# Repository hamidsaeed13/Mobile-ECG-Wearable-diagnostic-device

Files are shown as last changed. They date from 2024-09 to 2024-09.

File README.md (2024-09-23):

# Mobile ECG Project

### Supervisor:
-Prof. Dr. Shahid Khattak

### Team Members:
- Abdul Hameed
- M. Hamid Saeed
- Mujahid Haider

---

## Introduction:
This project aims to create a healthcare wearable Clinical Grade ECG device for continuous heart monitoring.
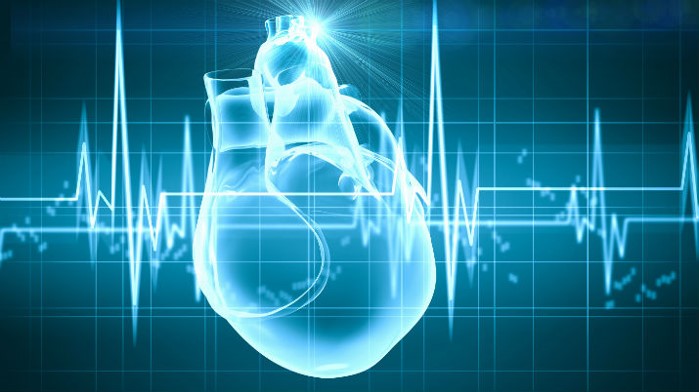
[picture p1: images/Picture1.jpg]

## Motivation:
- Existing ECG solutions are large and costly.
- Patients must be hospitalized, making it difficult to maintain long-term ECG logs.
- 24/7 ECG monitoring in remote areas is a challenge.

## Our Solution:
- 10-lead, 12-channel ECG diagnostic device.
- Bluetooth-enabled data transmission to smartphones for processing and log maintenance.
 
| Mobile Application | Demo Product |

---

## Aims and Objectives:
- Signal acquisition and conditioning.
- Multiplexing and Bluetooth communication.
- Real-time ECG graph visualization.
- Log maintenance and record-sharing with cardiologists.

---

## System Block Diagram:
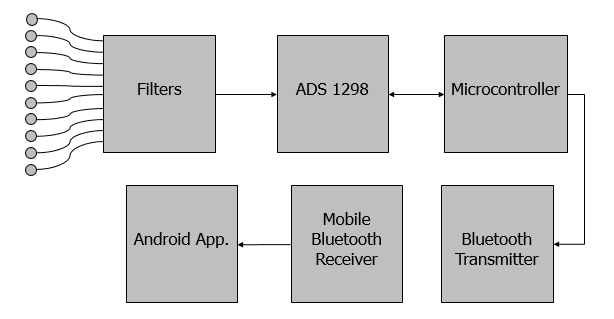
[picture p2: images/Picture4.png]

---
## Our Project:
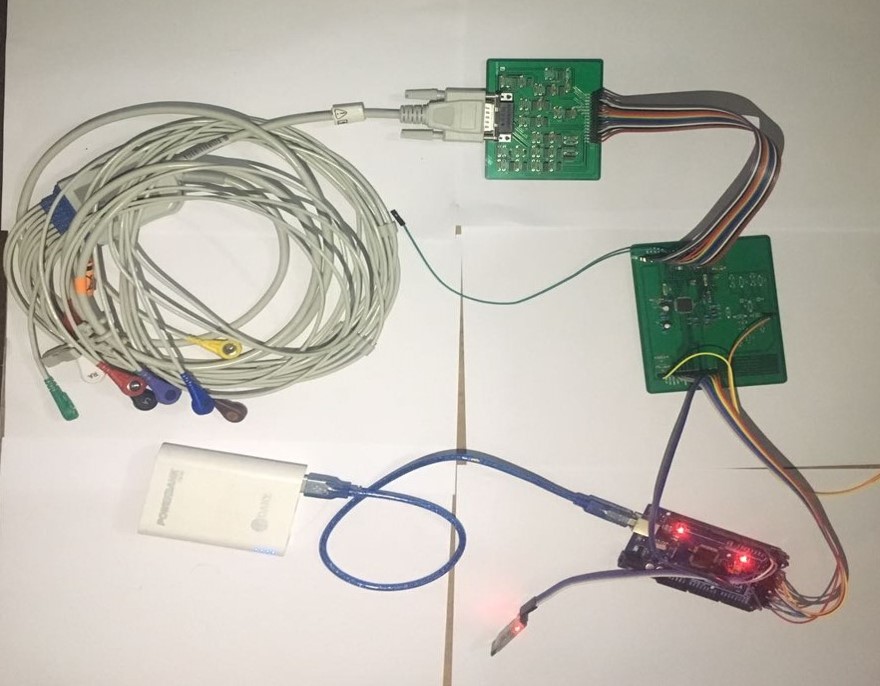
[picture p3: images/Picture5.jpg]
Project


---
## Filter Design:
- **Schematic**: 
  - R1 = 142.1KΩ
  - R2 = 120KΩ
  - C1 = C2 = 10nF
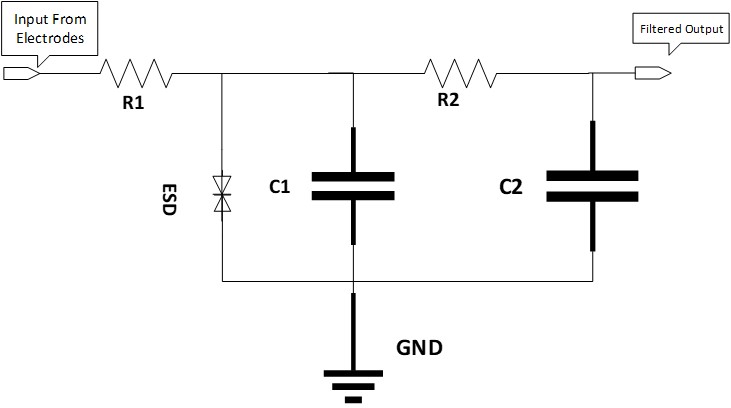
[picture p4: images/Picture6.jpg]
- **Design**: 
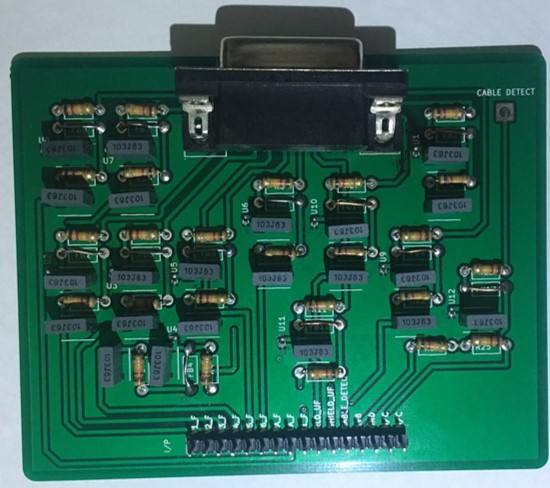
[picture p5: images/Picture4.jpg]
- **PCB**: 

---

## ADS1298:
- **Breakout Board**: 
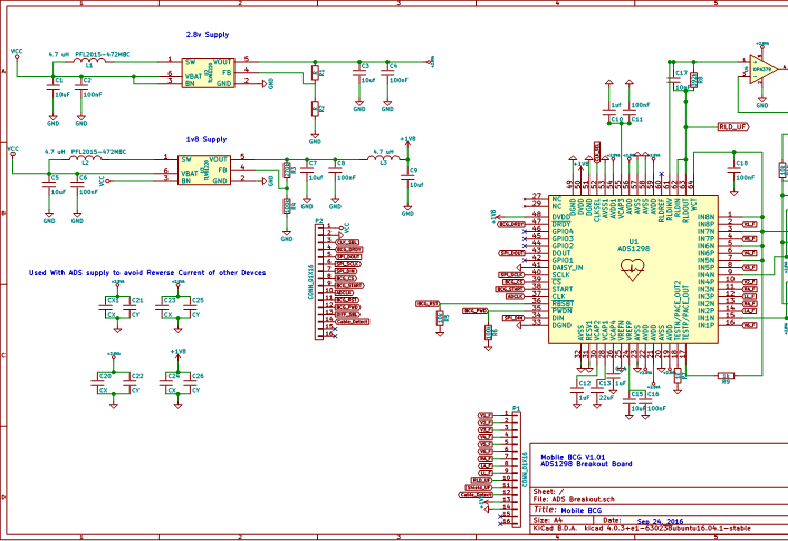
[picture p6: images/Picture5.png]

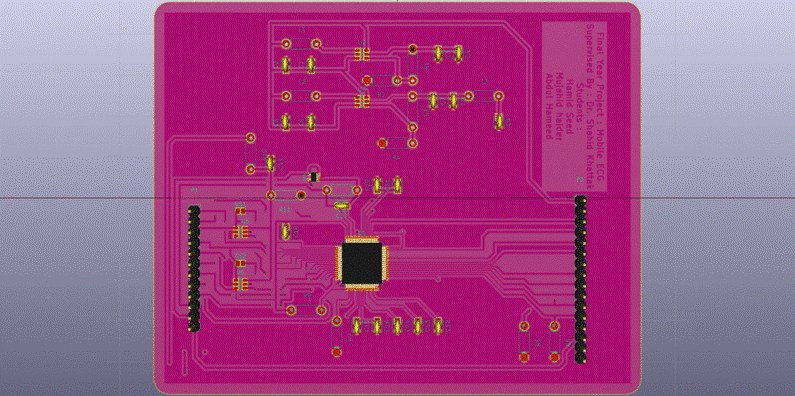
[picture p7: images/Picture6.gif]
- **PCB Layout**: 

---

## Android Application:
- Features:
  - Navigation menu with user details, doctor communication, and log maintenance.
  - 12-channel ECG view, Bluetooth connection, and real-time communication.
  - Options to find doctors and maintain a patient history.

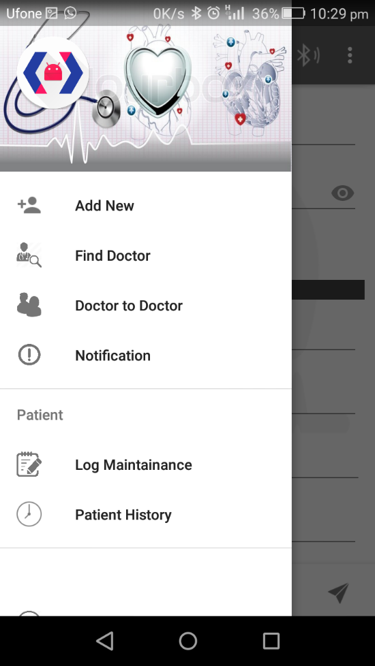
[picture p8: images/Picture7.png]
    
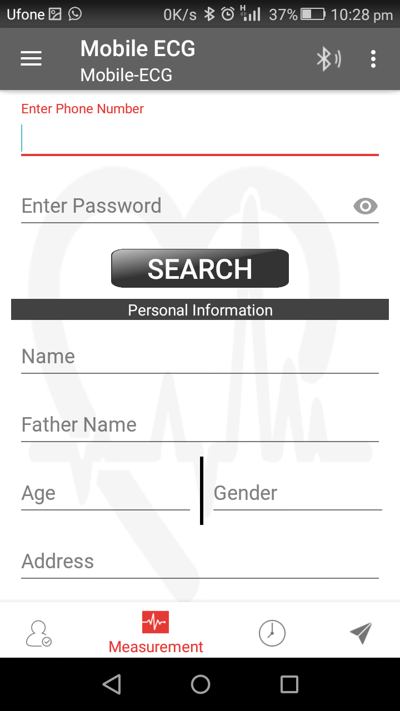
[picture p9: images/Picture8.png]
   
  
  
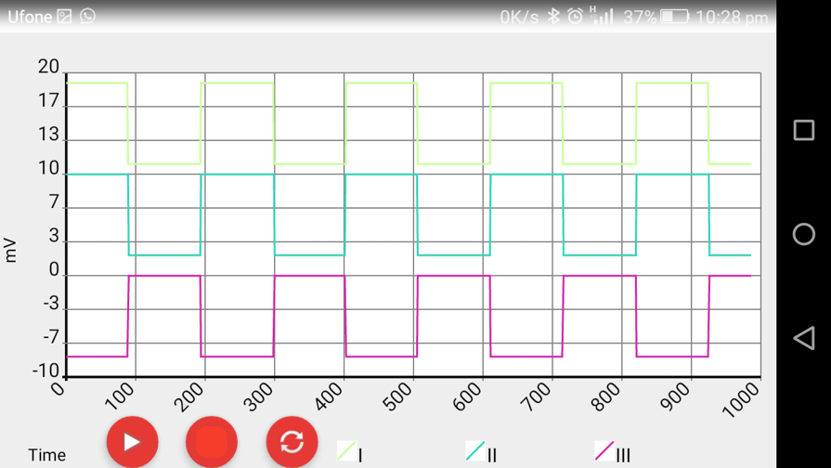
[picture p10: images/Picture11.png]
  
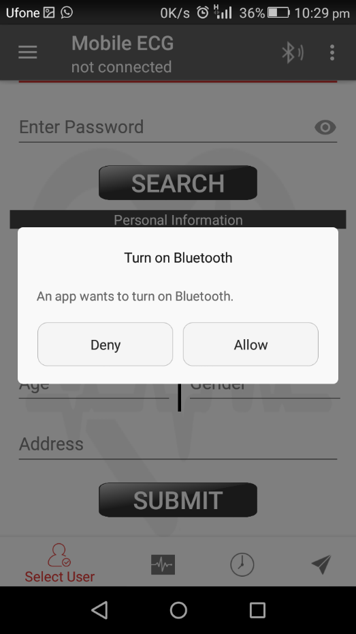
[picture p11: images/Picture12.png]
  
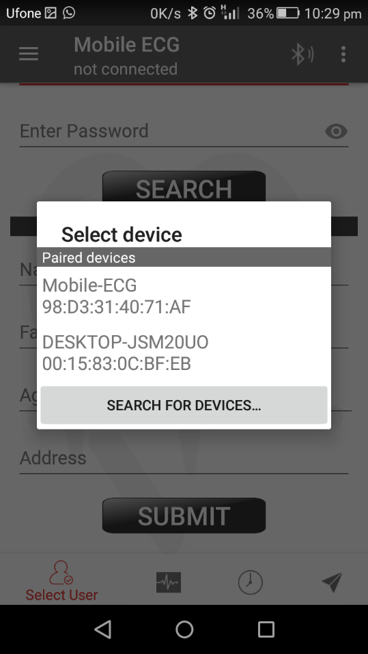
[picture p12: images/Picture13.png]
  
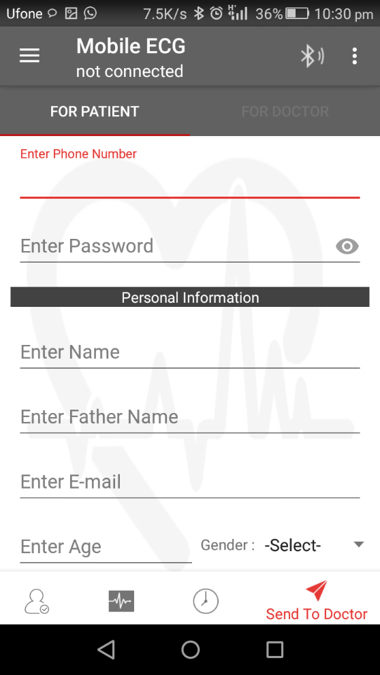
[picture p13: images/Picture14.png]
  
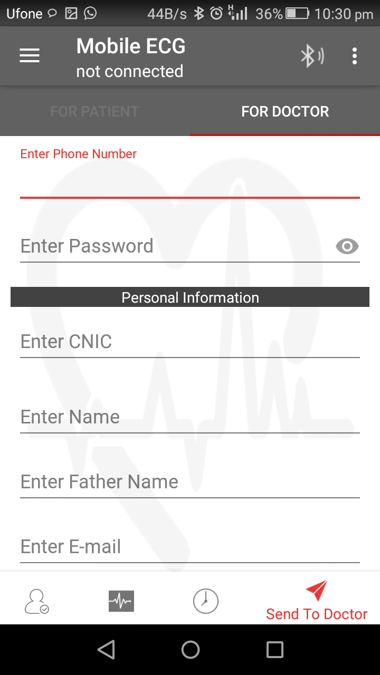
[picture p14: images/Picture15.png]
  
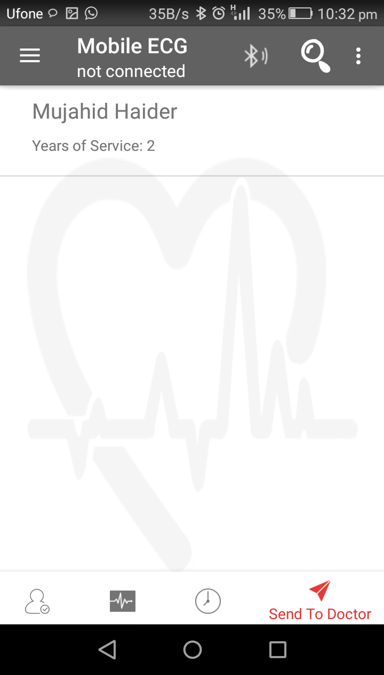
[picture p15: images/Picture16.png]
   

---
## Database
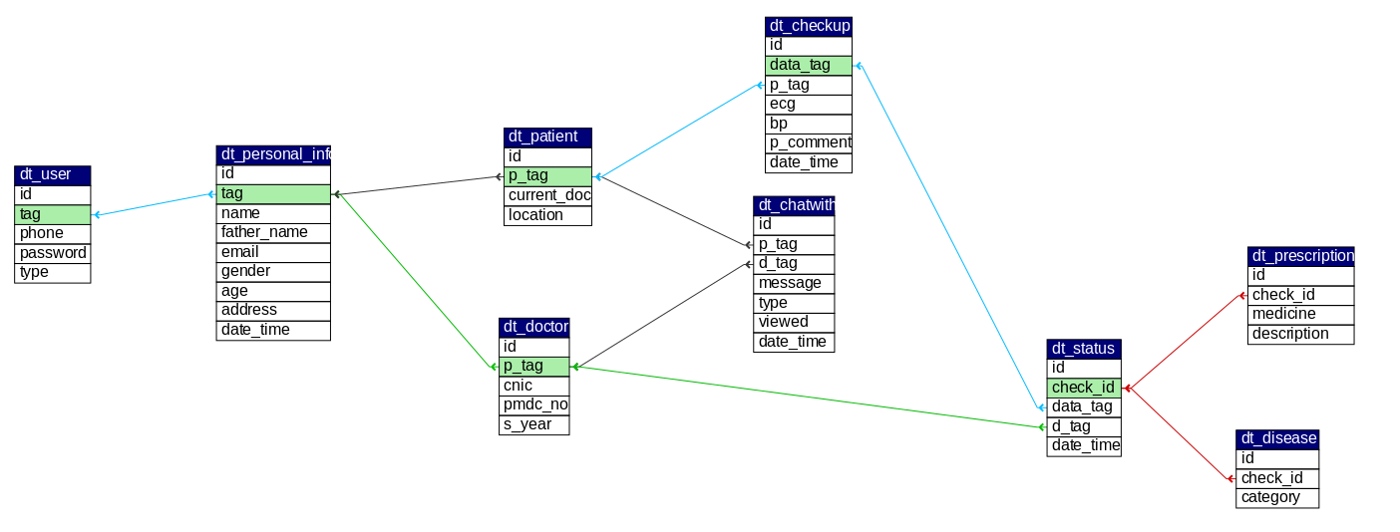
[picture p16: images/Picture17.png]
   

---

## Working Schedule:
- Phase I (March 2016 - May 2016)
- Phase II (August 2016 - Onwards)

---

## Questions:
Feel free to reach out for further details.
*contact*: +92301 2216201
email: hamidsaeed13@gmail.com

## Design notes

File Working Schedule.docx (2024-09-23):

# FYP Title: Mobile ECG

# Objectives:

Make wearable Hardware Device to Acquire ECG Signal, Transfer this signal to Android Mobile. Real time ECG Monitoring. Apply Signal Conditioning Algorithms. Maintaining Log of ECG Signal and send to a heart Specialist

We are going to provide basic 3 facilities

1. Home ECG Service

This service will allow patients to provide their doctors with frequent, reliable high-quality records. Also check out our affordable clinical-grade device designed for doctors and patients.

2. Interpretation Service

Have your ECG record (and medical history) analyzed over the internet by the heart specialist of your choice.

3. Doctor-to-doctor Service

This service will allow other doctors to send data to heart specialists and have a consultation with them.

# Schedule of Phase 1

Start | End | | Presentation on ADS1298
03-03-16 | 06-04-16 | Bluetooth interfacing | | Graph View
06-04-16 | 19-04-16 | Layout of Application
19-04-16 | 26-04-16 | | | send data from Arduino to android
26-04-16 | 03-05-16 | Circular buffer | | MATLAB implementation of signal reconditioning
26-04-16 | 10-05-16 | Filter Simulation of 3-lead
10-05-16 | 17-05-16 | Filter simulation and Power Supply for ADS
17-05-16 | 31-05-16 | Instrumentation amplifier design
01-06-16 | 10-06-16 | programming of microcontroller for ADS | View ECG signal on android app
01-06-16 | 25-06-16 | setting of ADS ,signal input ,Power supply

End of Semester

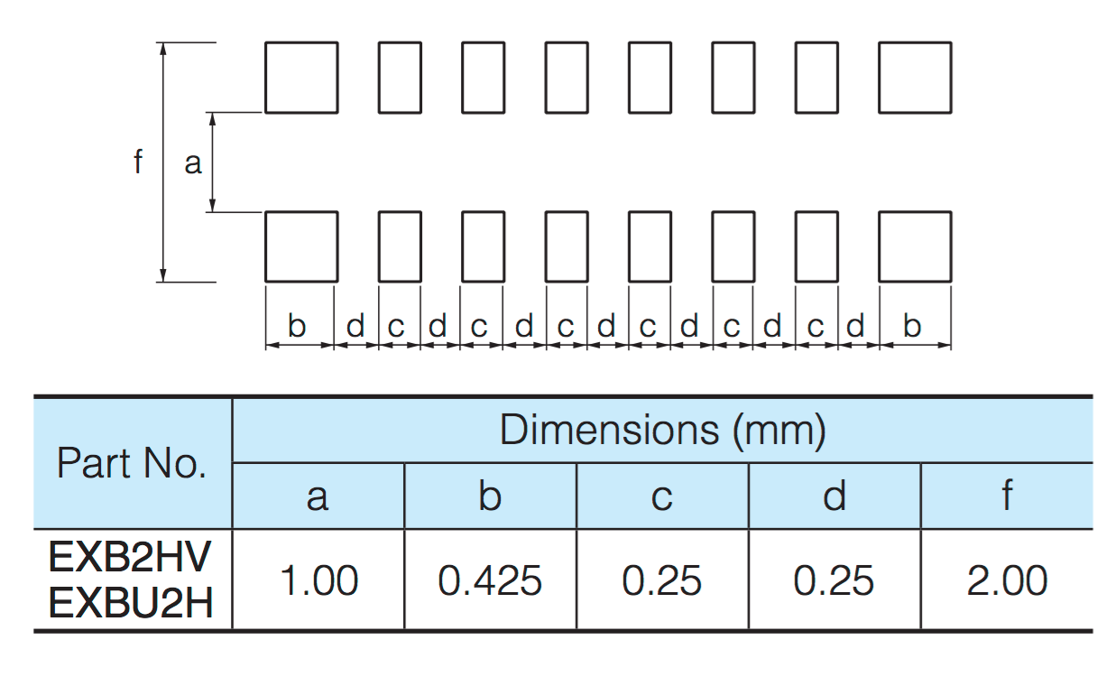
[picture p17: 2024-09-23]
Mobile ECG Hardware Final/Hardware/Datasheets/Resistor network/EXB2HV.png

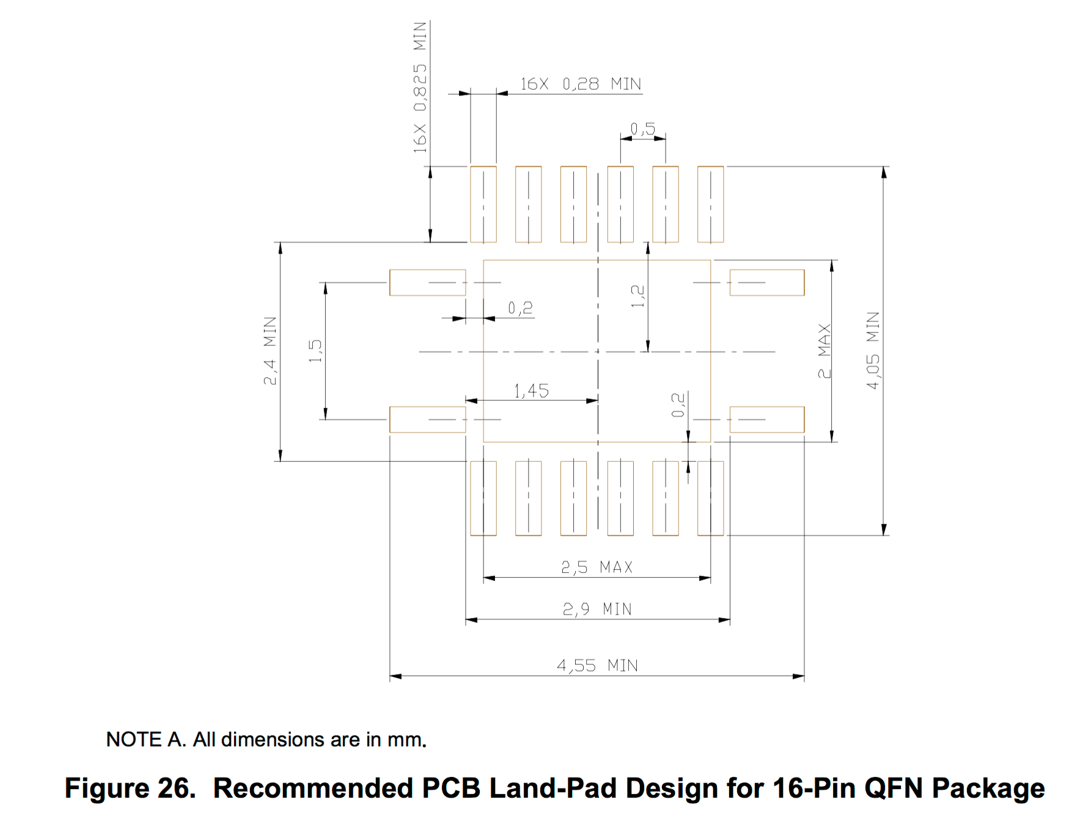
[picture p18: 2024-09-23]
Mobile ECG Hardware Final/Hardware/Datasheets/Level shifter/Footprint.png

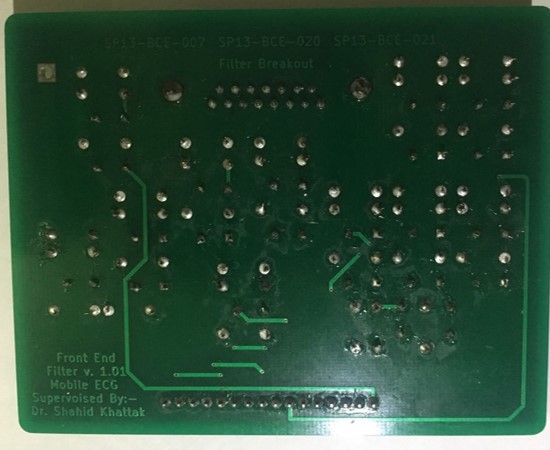
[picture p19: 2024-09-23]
images/Picture7.jpg

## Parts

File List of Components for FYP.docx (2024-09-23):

Name | Qty | $ | Search Link
INA333 | 3 | 4.42 | Digi key Part No : 296-23564-1-ND (http://www.digikey.com/product-detail/en/texas-instruments/INA333AIDGKR/296-23564-1-ND/1886116) Manufacturer No: INA333AIDGKR (http://www.digikey.com/product-detail/en/texas-instruments/INA333AIDGKR/296-23564-1-ND/1886116)
HDMI 12 lead ECG/EKG Cable with lead wires | 1 | 35
ECG/EKG electrodes adapter | 12 | -
ADS1298 | 2 | 41.81 | Digi key Part No : 296-27734-ND (http://www.digikey.com/product-detail/en/texas-instruments/ADS1298IPAG/296-27734-ND/2360825) Manufacturer No: ADS1298IPAG (http://www.digikey.com/product-detail/en/texas-instruments/ADS1298IPAG/296-27734-ND/2360825)
KIT PERFORMANCE DEMO FOR ADS1298 | 1 | 200.56 | Digi key Part No : 296-30132-ND (http://www.digikey.com/product-detail/en/texas-instruments/ADS1298ECGFE-PDK/296-30132-ND/2353228) Manufacturer No: ADS1298ECGFE-PDK (http://www.digikey.com/product-detail/en/texas-instruments/ADS1298ECGFE-PDK/296-30132-ND/2353228)
TQFP64 adapter IC test socket | 1 | 18.68 | Search Link (http://www.ebay.com/itm/QFP64-TQFP64-adapter-IC-test-socket-burning-seat-0-5m-programmer-LQFP64-seat-/351518438484)
HDMI Connector | 3 | 0.73 | Digi key Part No : 609-4614-1-ND (http://www.digikey.com/product-detail/en/amphenol-fci/10029449-111RLF/609-4614-1-ND/2785376) Manufacturer No: 10029449-111RLF (http://www.digikey.com/product-detail/en/amphenol-fci/10029449-111RLF/609-4614-1-ND/2785376)
TiWi-uB2 (Bluetooth Module) | 1 | 12.30 | Digi key Part No : 450-0104-ND (http://www.digikey.com/product-detail/en/lsr/450-0104/450-0104-ND/3661880) Manufacturer No: 450-0104 (http://www.digikey.com/product-detail/en/lsr/450-0104/450-0104-ND/3661880)
TXB0106PWR (Bidirectional Voltage-Level Translator) | 3 | 1.92 | Digi key Part No : 296-23759-1-ND (http://www.digikey.com/product-detail/en/texas-instruments/TXB0106PWR/296-23759-1-ND/1951146) Manufacturer No: TXB0106PWR (http://www.digikey.com/product-detail/en/texas-instruments/TXB0106PWR/296-23759-1-ND/1951146)
STM32F4 01/11 Microcontroller | 2 | 6.25 | Digi key Part No : 497-14047-ND (http://www.digikey.com/product-detail/en/stmicroelectronics/STM32F401RCT6/497-14047-ND/4494300) / 497-14909-ND (http://www.digikey.com/product-detail/en/stmicroelectronics/STM32F411RET6/497-14909-ND/4935722) Manufacturer No: STM32F401RCT6 (http://www.digikey.com/product-detail/en/stmicroelectronics/STM32F401RCT6/497-14047-ND/4494300)/ STM32F411RET6 (http://www.digikey.com/product-detail/en/stmicroelectronics/STM32F411RET6/497-14909-ND/4935722)
BOARD NUCLEO STM32F4 01/11 SERIES | 1 | 13.83 | Digi key Part No : 497-14360-ND (http://www.digikey.com/product-detail/en/stmicroelectronics/NUCLEO-F401RE/497-14360-ND/4695525) / 497-14711-ND (http://www.digikey.com/product-detail/en/stmicroelectronics/NUCLEO-F411RE/497-14711-ND/4866485) Manufacturer No: NUCLEO-F401RE (http://www.digikey.com/product-detail/en/stmicroelectronics/NUCLEO-F401RE/497-14360-ND/4695525) / NUCLEO-F411RE (http://www.digikey.com/product-detail/en/stmicroelectronics/NUCLEO-F411RE/497-14711-ND/4866485)
USB2641 Flash Memory for Controller | 1 | 3.18 | Digi key Part No : USB2641-HZH-02-ND (http://www.digikey.com/product-detail/en/microchip-technology/USB2641-HZH-02/USB2641-HZH-02-ND/3873174) Manufacturer No: USB2641-HZH-02 (http://www.digikey.com/product-detail/en/microchip-technology/USB2641-HZH-02/USB2641-HZH-02-ND/3873174)
LIS2DH12TR | 1 | 1.60 | Digi key Part No : 497-14851-1-ND (http://www.digikey.com/product-detail/en/stmicroelectronics/LIS2DH12TR/497-14851-1-ND/4899838) Manufacturer No: LIS2DH12TR (http://www.digikey.com/product-detail/en/stmicroelectronics/LIS2DH12TR/497-14851-1-ND/4899838)
ESD suppressor | 20 | 0.47 | Digi key Part No : 296-30406-1-ND (http://www.digikey.com/product-detail/en/texas-instruments/TPD1E10B06DPYR/296-30406-1-ND/3283560) Manufacturer No: TPD1E10B06DPYR (http://www.digikey.com/product-detail/en/texas-instruments/TPD1E10B06DPYR/296-30406-1-ND/3283560)
TS5A3159 | 3 | 0.85 | Digi key Part No : 296-19265-1-ND (http://www.digikey.com/product-detail/en/texas-instruments/TS5A3159ADBVR/296-19265-1-ND/936397) Manufacturer No: TS5A3159ADBVR (http://www.digikey.com/product-detail/en/texas-instruments/TS5A3159ADBVR/296-19265-1-ND/936397)
OPA2379 | 2 | 1.41 | Digi key Part No : 296-19875-1-ND (http://www.digikey.com/product-detail/en/texas-instruments/OPA379AIDCKT/296-19875-1-ND/1120791) Manufacturer No: OPA379AIDCKT (http://www.digikey.com/product-detail/en/texas-instruments/OPA379AIDCKT/296-19875-1-ND/1120791)
USBULC6-2M6 | 2 | 1.21 | Digi key Part No : 497-7044-1-ND (http://www.digikey.com/product-detail/en/stmicroelectronics/USBULC6-2M6/497-7044-1-ND/1880382) Manufacturer No: USBULC6-2M6 (http://www.digikey.com/product-detail/en/stmicroelectronics/USBULC6-2M6/497-7044-1-ND/1880382)
AB38T-32.768KHZ (XT oscillator) | 2 | 0.57 | Digi key Part No : 300-8340-1-ND (http://www.digikey.com/product-detail/en/citizen-finedevice-co-ltd/CMR200T32768DZFT/300-8340-1-ND/862984) Manufacturer No: CMR200T32768DZFT (http://www.digikey.com/product-detail/en/citizen-finedevice-co-ltd/CMR200T32768DZFT/300-8340-1-ND/862984)
CRYSTAL 10MHz | 2 | 0.28 | Digi key Part No : 535-9065-1-ND (http://www.digikey.com/product-detail/en/abracon-llc/ABLS-10.000MHZ-B2-T/535-9065-1-ND/675582) Manufacturer No: ABLS-10.000MHZ-B2-T (http://www.digikey.com/product-detail/en/abracon-llc/ABLS-10.000MHZ-B2-T/535-9065-1-ND/675582)
EXB-2HV510JV (Resistor Array 51ohm) | 5 | 0.037 | Digi key Part No : EXB-2HV510JV-ND (http://www.digikey.com/product-search/en?keywords=%20EXB-2HV510JV) Manufacturer No: EXB-2HV510JV (http://www.digikey.com/product-search/en?keywords=%20EXB-2HV510JV)
2450AT42A100E (Bluetooth Antenna) | 2 | 1.10 | Digi key Part No : 712-1007-1-ND (http://www.digikey.com/product-detail/en/johanson-technology-inc/2450AT42A100E/712-1007-1-ND/1560836) Manufacturer No: 2450AT42A100E (http://www.digikey.com/product-detail/en/johanson-technology-inc/2450AT42A100E/712-1007-1-ND/1560836)
EXB2HV104JV (Resistor Array 100 ohm) | 2 | 0.55 | Digi key Part No : Y1104CT-ND (http://www.digikey.com/product-detail/en/panasonic-electronic-components/EXB-2HV104JV/Y1104CT-ND/285405) Manufacturer No: EXB-2HV104JV (http://www.digikey.com/product-detail/en/panasonic-electronic-components/EXB-2HV104JV/Y1104CT-ND/285405)
uSD MicroSD Connector | 1 | 1.11 | Part No : MEM2051-00-195-00-A (http://www.newark.com/jsp/search/productdetail.jsp?sku=05W3557) (http://www.digikey.com/product-detail/en/panasonic-electronic-components/EXB-2HV104JV/Y1104CT-ND/285405)
AT24CS01-STUM-T (EEPROM 1KBIT) | 1 | 0.33 | Digi key Part No : AT24CS01-STUM-TCT-ND (http://www.digikey.com/product-detail/en/atmel/AT24CS01-STUM-T/AT24CS01-STUM-TCT-ND/3973039) Manufacturer No: AT24CS01-STUM-T (http://www.digikey.com/product-detail/en/atmel/AT24CS01-STUM-T/AT24CS01-STUM-TCT-ND/3973039)
CRYSTAL 24MHz | 2 | 0.44 | Digi key Part No : 535-9881-1-ND (http://www.digikey.com/product-detail/en/abracon-llc/ABLS2-24.000MHZ-D4YF-T/535-9881-1-ND/2001504) Manufacturer No: ABLS2-24.000MHZ-D4YF-T (http://www.digikey.com/product-detail/en/abracon-llc/ABLS2-24.000MHZ-D4YF-T/535-9881-1-ND/2001504)
LittelFuse Inc. 1206L075THYR | 4 | 0.48 | Digi key Part No : F3370CT-ND (http://www.digikey.com/product-detail/en/littelfuse-inc/1206L075THYR/F3370CT-ND/2090987) Manufacturer No: 1206L075THYR (http://www.digikey.com/product-detail/en/littelfuse-inc/1206L075THYR/F3370CT-ND/2090987)
Connector 1x5 | 4 | 1.49 | Digi key Part No : 478-5453-1-ND (http://www.digikey.com/product-detail/en/avx-corporation/009155005541006/478-5453-1-ND/2001014) Manufacturer No: 009155005541006 (http://www.digikey.com/product-detail/en/avx-corporation/009155005541006/478-5453-1-ND/2001014)
Connector 1 row | 3 | | Link (http://www.traceparts.cn/Content/en/Product/wurth-elektronik/WRTH-ELEKTRONIK-ELECTROMECHANICAL-COMPONENTS-BTBBoard-To-Board-Socket-Header-254/10-05032015-0662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) / Link2 (http://www.traceparts.cn/Content/en/Product/wurth-elektronik/WRTH-ELEKTRONIK-ELECTROMECHANICAL-COMPONENTS-BTBBoard-To-Board-Socket-Header-200/10-05032015-0669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) / link3 (http://www.traceparts.cn/Content/en/Product/wurth-elektronik/WRTH-ELEKTRONIK-ELECTROMECHANICAL-COMPONENTS-BTBBoard-To-Board-Socket-Header-200/10-05032015-0669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)

Power Schematic Components
TLV61220 (DC to DC voltage Regulator) | 5 | 0.92 | Digi key Part No : 296-30547-1-ND (http://www.digikey.com/product-detail/en/texas-instruments/TLV61220DBVR/296-30547-1-ND/3458120) Manufacturer No: TLV61220DBVR (http://www.digikey.com/product-detail/en/texas-instruments/TLV61220DBVR/296-30547-1-ND/3458120)
DS2710 | 2 | 3.87 | Digi key Part No : DS2710G+T&RCT-ND (http://www.digikey.com/product-detail/en/maxim-integrated/DS2710G%2BT%26R/DS2710G%2BT%26RCT-ND/4807776) Manufacturer No: DS2710G+T&R (http://www.digikey.com/product-detail/en/maxim-integrated/DS2710G%2BT%26R/DS2710G%2BT%26RCT-ND/4807776)
LM3671 | 2 | 0.92 | Digi key Part No : LM3671MF-3.3/NOPBCT-ND (http://www.digikey.com/product-detail/en/texas-instruments/LM3671MF-3.3%2FNOPB/LM3671MF-3.3%2FNOPBCT-ND/1590190) Manufacturer No: LM3671MF-3.3/NOPB (http://www.digikey.com/product-detail/en/texas-instruments/LM3671MF-3.3%2FNOPB/LM3671MF-3.3%2FNOPBCT-ND/1590190)
TPS61070 | 2 | 1.38 | Digi key Part No : 296-17151-1-ND (http://www.digikey.com/product-detail/en/texas-instruments/TPS61070DDCR/296-17151-1-ND/665930) Manufacturer No: TPS61070DDCR (http://www.digikey.com/product-detail/en/texas-instruments/TPS61070DDCR/296-17151-1-ND/665930)
BQ2000 | 2 | 1.63125 | Digi key Part No : 296-25915-2-ND (http://www.digikey.com/product-detail/en/BQ2000SN-B5TR/296-25915-2-ND/1689991) Manufacturer No: BQ2000SN-B5TR (http://www.digikey.com/product-detail/en/BQ2000SN-B5TR/296-25915-2-ND/1689991)
Estimated Cost | | 359.3283$ | 37609.10 /.Rs

Comparison
Arduino (Atmega2560) | STM32F401
100 pin IC | 64 /100 pins
8 Bit controller | 32bit Controller
1 MIPS per MHz | 1.25 DMIPS/MHz
Flash 256 Kb | 256KB Flash
EEPROM 4kb
RAM 8 kb | 64KB RAM
I/O Pins 86 | Up to 81 I/O ports
ADC Channel 16 | 16
Digital Voltage Supply 5v | 1.7 to 3.6 V
16 MHZ | frequency up to 84 MHz
| Advanced connectivity – USB 2.0 full-speed device/host/OTG controller with on-chip PHY
17.46 $ | 6.25 $

12 Channel ECG cable have 10 Wires because of Eindhoven’s Triangle

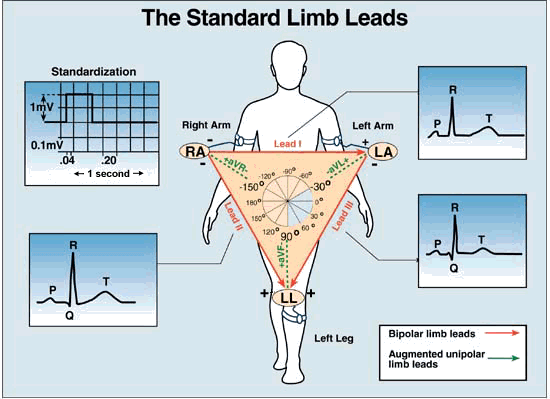
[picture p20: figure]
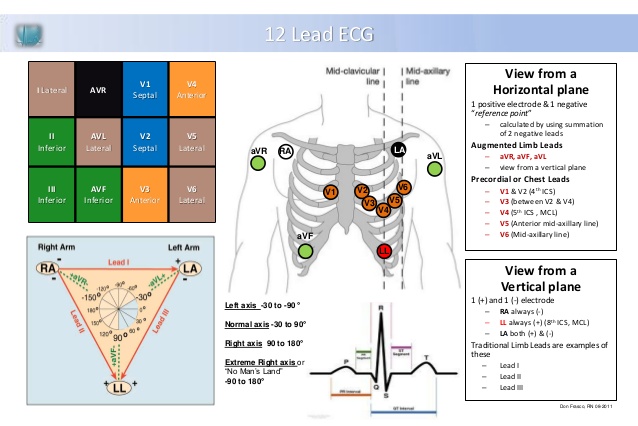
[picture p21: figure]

Components List For FYP

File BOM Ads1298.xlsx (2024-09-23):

Value | Discription | Quantity | Ceramic Capacitor | Inductor
4.7 uH | Inductor through Hole | 5
10uF | Disc_Solid_ceramic_Capacitors_ThroughHole | 9
100nF | Disc_Solid_ceramic_Capacitors_ThroughHole | 20
270k | Resistors_ThroughHole 1/4 Watt | 3
100k | Resistors_ThroughHole 1/4 Watt | 8
1uf | Disc_Solid_ceramic_Capacitors_ThroughHole | 8
10nF | Disc_Solid_ceramic_Capacitors_ThroughHole | 5
392k | Resistors_ThroughHole 1/4 Watt | 5
1k | Resistors_ThroughHole 1/4 Watt | 5
22uF | Disc_Solid_ceramic_Capacitors_ThroughHole | 5
10k | Resistors_ThroughHole 1/4 Watt | 6

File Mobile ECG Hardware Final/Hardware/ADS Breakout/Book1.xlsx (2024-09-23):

version | source | date | tool | number | name | tstamps | title | company | rev | date2 | source3 | number4 | value | ref | value5 | footprint | lib | part | names | tstamps6 | tstamp | lib7 | part8 | field | name9 | num | name10 | type | description | fp | logical | uri | code | name11 | ref12 | pin
D | /media/hamid/Entertainment/STUDY DATA/FYP/Mobile ECG Hardware Final/Hardware/ADS Breakout/ADS Breakout.sch | و 23:49:54 PKT ت 08 نومبر 2016 | Eeschema 4.0.4+e1-6308~48~ubuntu16.04.1-stable | 1 | / | / |  |  |  |  | ADS Breakout.sch | 1
D | /media/hamid/Entertainment/STUDY DATA/FYP/Mobile ECG Hardware Final/Hardware/ADS Breakout/ADS Breakout.sch | و 23:49:54 PKT ت 08 نومبر 2016 | Eeschema 4.0.4+e1-6308~48~ubuntu16.04.1-stable | 1 | / | / |  |  |  |  | ADS Breakout.sch | 2
D | /media/hamid/Entertainment/STUDY DATA/FYP/Mobile ECG Hardware Final/Hardware/ADS Breakout/ADS Breakout.sch | و 23:49:54 PKT ت 08 نومبر 2016 | Eeschema 4.0.4+e1-6308~48~ubuntu16.04.1-stable | 1 | / | / |  |  |  |  | ADS Breakout.sch | 3
D | /media/hamid/Entertainment/STUDY DATA/FYP/Mobile ECG Hardware Final/Hardware/ADS Breakout/ADS Breakout.sch | و 23:49:54 PKT ت 08 نومبر 2016 | Eeschema 4.0.4+e1-6308~48~ubuntu16.04.1-stable | 1 | / | / |  |  |  |  | ADS Breakout.sch | 4
D |  |  |  |  |  |  |  |  |  |  |  |  |  | U1 | ADS1298 | Housings_QFP:TQFP-64_10x10mm_Pitch0.5mm | ads1298 | ADS1298 | / | / | 57C71969
D |  |  |  |  |  |  |  |  |  |  |  |  |  | U2 | TLV61220 | Housings_SOT-23_SOT-143_TSOT-6:SOT-23-6 | holter-cache | TLV61220 | / | / | 57C71A8D
D |  |  |  |  |  |  |  |  |  |  |  |  |  | L1 | 4.7 uH PFL2015-472MEC | Resistors_ThroughHole:Resistor_Horizontal_RM7mm | device | INDUCTOR | / | / | 57C71E61
D |  |  |  |  |  |  |  |  |  |  |  |  |  | C1 | 10uF | Capacitors_ThroughHole:C_Disc_D3_P2.5 | device | C | / | / | 57C71FD0
D |  |  |  |  |  |  |  |  |  |  |  |  |  | C2 | 100nF | Capacitors_ThroughHole:C_Disc_D3_P2.5 | device | C | / | / | 57C72021
D |  |  |  |  |  |  |  |  |  |  |  |  |  | R1 | R | Resistors_ThroughHole:Resistor_Horizontal_RM7mm | device | R | / | / | 57C724C6
D |  |  |  |  |  |  |  |  |  |  |  |  |  | R2 | R | Resistors_ThroughHole:Resistor_Horizontal_RM7mm | device | R | / | / | 57C72517
D |  |  |  |  |  |  |  |  |  |  |  |  |  | C3 | 10uf | Capacitors_ThroughHole:C_Disc_D3_P2.5 | device | C | / | / | 57C726DC
D |  |  |  |  |  |  |  |  |  |  |  |  |  | C4 | 100nF | Capacitors_ThroughHole:C_Disc_D3_P2.5 | device | C | / | / | 57C726E2
D |  |  |  |  |  |  |  |  |  |  |  |  |  | U3 | TLV61220 | Housings_SOT-23_SOT-143_TSOT-6:SOT-23-6 | holter-cache | TLV61220 | / | / | 57C7367D
D |  |  |  |  |  |  |  |  |  |  |  |  |  | L2 | 4.7 uH PFL2015-472MEC | Resistors_ThroughHole:Resistor_Horizontal_RM7mm | device | INDUCTOR | / | / | 57C73683
D |  |  |  |  |  |  |  |  |  |  |  |  |  | C5 | 10uF | Capacitors_ThroughHole:C_Disc_D3_P2.5 | device | C | / | / | 57C7368A
D |  |  |  |  |  |  |  |  |  |  |  |  |  | C6 | 100nF | Capacitors_ThroughHole:C_Disc_D3_P2.5 | device | C | / | / | 57C73690
D |  |  |  |  |  |  |  |  |  |  |  |  |  | R3 | 270k | Resistors_ThroughHole:Resistor_Horizontal_RM7mm | device | R | / | / | 57C736B9
D |  |  |  |  |  |  |  |  |  |  |  |  |  | R4 | 100k | Resistors_ThroughHole:Resistor_Horizontal_RM7mm | device | R | / | / | 57C736BF
D |  |  |  |  |  |  |  |  |  |  |  |  |  | C7 | 10uf | Capacitors_ThroughHole:C_Disc_D3_P2.5 | device | C | / | / | 57C736D1
D |  |  |  |  |  |  |  |  |  |  |  |  |  | C8 | 100nF | Capacitors_ThroughHole:C_Disc_D3_P2.5 | device | C | / | / | 57C736D7
D |  |  |  |  |  |  |  |  |  |  |  |  |  | L3 | 4.7 uH | Resistors_ThroughHole:Resistor_Horizontal_RM7mm | device | INDUCTOR | / | / | 57C74186
D |  |  |  |  |  |  |  |  |  |  |  |  |  | C9 | 10uf | Capacitors_ThroughHole:C_Disc_D3_P2.5 | device | C | / | / | 57C743CD
D |  |  |  |  |  |  |  |  |  |  |  |  |  | C10 | 1uf | Capacitors_ThroughHole:C_Disc_D3_P2.5 | device | C | / | / | 57C5857E
D |  |  |  |  |  |  |  |  |  |  |  |  |  | C11 | 100nF | Capacitors_ThroughHole:C_Disc_D3_P2.5 | device | C | / | / | 57C58584
D |  |  |  |  |  |  |  |  |  |  |  |  |  | U4 | OPA379 | TO_SOT_Packages_SMD:SC-70-5 | holter-cache | SC70_OPAMP | / | / | 57C592A0
D |  |  |  |  |  |  |  |  |  |  |  |  |  | C17 | 10nF | Capacitors_ThroughHole:C_Disc_D3_P2.5 | device | C | / | / | 57C5939F
D |  |  |  |  |  |  |  |  |  |  |  |  |  | R8 | 392k | Resistors_ThroughHole:Resistor_Horizontal_RM7mm | device | R | / | / | 57C593EE
D |  |  |  |  |  |  |  |  |  |  |  |  |  | C18 | 100nF | Capacitors_ThroughHole:C_Disc_D3_P2.5 | device | C | / | / | 57CE1B00
D |  |  |  |  |  |  |  |  |  |  |  |  |  | R9 | 1k | Resistors_ThroughHole:Resistor_Horizontal_RM7mm | device | R | / | / | 57CE2366
D |  |  |  |  |  |  |  |  |  |  |  |  |  | R7 | 1k | Resistors_ThroughHole:Resistor_Horizontal_RM7mm | device | R | / | / | 57CE2AAD
D |  |  |  |  |  |  |  |  |  |  |  |  |  | C15 | 10uF | Capacitors_ThroughHole:C_Disc_D3_P2.5 | device | C | / | / | 57CE35CD
D |  |  |  |  |  |  |  |  |  |  |  |  |  | C16 | 100nF | Capacitors_ThroughHole:C_Disc_D3_P2.5 | device | C | / | / | 57CE36D4
D |  |  |  |  |  |  |  |  |  |  |  |  |  | C14 | 1uF | Capacitors_ThroughHole:C_Disc_D3_P2.5 | device | C | / | / | 57CE3AF8
D |  |  |  |  |  |  |  |  |  |  |  |  |  | C13 | 22uF | Capacitors_ThroughHole:C_Disc_D3_P2.5 | device | C | / | / | 57CE3B57
D |  |  |  |  |  |  |  |  |  |  |  |  |  | C12 | 1uF | Capacitors_ThroughHole:C_Disc_D3_P2.5 | device | C | / | / | 57CE3BB6
D |  |  |  |  |  |  |  |  |  |  |  |  |  | U6 | TS5A3159 | Housings_SOT-23_SOT-143_TSOT-6:SOT-23-6 | holter-cache | TS5A3159 | / | / | 57CE7B38
D |  |  |  |  |  |  |  |  |  |  |  |  |  | U5 | TS5A3159 | Housings_SOT-23_SOT-143_TSOT-6:SOT-23-6 | holter-cache | TS5A3159 | / | / | 57CE85AF
D |  |  |  |  |  |  |  |  |  |  |  |  |  | R11 | 100k | Resistors_ThroughHole:Resistor_Horizontal_RM7mm | device | R | / | / | 57CE93E4
D |  |  |  |  |  |  |  |  |  |  |  |  |  | R10 | 10k | Resistors_ThroughHole:Resistor_Horizontal_RM7mm | device | R | / | / | 57CE9491
D |  |  |  |  |  |  |  |  |  |  |  |  |  | C19 | 100nF | Capacitors_ThroughHole:C_Disc_D3_P2.5 | device | C | / | / | 57CE94F0
D |  |  |  |  |  |  |  |  |  |  |  |  |  | R5 | 10k | Resistors_ThroughHole:Resistor_Horizontal_RM7mm | device | R | / | / | 57CEA91A
D |  |  |  |  |  |  |  |  |  |  |  |  |  | R6 | 100k | Resistors_ThroughHole:Resistor_Horizontal_RM7mm | device | R | / | / | 57CEA9A9
D |  |  |  |  |  |  |  |  |  |  |  |  |  | P2 | CONN_01X16 | Pin_Headers:Pin_Header_Straight_1x16 | conn | CONN_01X16 | / | / | 57CEBBF3
D |  |  |  |  |  |  |  |  |  |  |  |  |  | GS1 | GS2 | Connect:GS2 | conn | GS2 | / | / | 57CEBD88
D |  |  |  |  |  |  |  |  |  |  |  |  |  | GS2 | GS2 | Connect:GS2 | conn | GS2 | / | / | 57CEBE67
D |  |  |  |  |  |  |  |  |  |  |  |  |  | CX1 | CX | Capacitors_ThroughHole:C_Disc_D3_P2.5 | device | C | / | / | 57E57EDE
D |  |  |  |  |  |  |  |  |  |  |  |  |  | C21 | CY | Capacitors_ThroughHole:C_Disc_D3_P2.5 | device | C | / | / | 57E57F9D
D |  |  |  |  |  |  |  |  |  |  |  |  |  | C23 | CX | Capacitors_ThroughHole:C_Disc_D3_P2.5 | device | C | / | / | 57E58034
D |  |  |  |  |  |  |  |  |  |  |  |  |  | C25 | CY | Capacitors_ThroughHole:C_Disc_D3_P2.5 | device | C | / | / | 57E580CB
D |  |  |  |  |  |  |  |  |  |  |  |  |  | C20 | CX | Capacitors_ThroughHole:C_Disc_D3_P2.5 | device | C | / | / | 57E58172
D |  |  |  |  |  |  |  |  |  |  |  |  |  | C22 | CY | Capacitors_ThroughHole:C_Disc_D3_P2.5 | device | C | / | / | 57E58413
D |  |  |  |  |  |  |  |  |  |  |  |  |  | C24 | CX | Capacitors_ThroughHole:C_Disc_D3_P2.5 | device | C | / | / | 57E584BC
D |  |  |  |  |  |  |  |  |  |  |  |  |  | C26 | CY | Capacitors_ThroughHole:C_Disc_D3_P2.5 | device | C | / | / | 57E58541
D |  |  |  |  |  |  |  |  |  |  |  |  |  | P1 | CONN_01X16 | Pin_Headers:Pin_Header_Straight_1x16 | conn | CONN_01X16 | / | / | 57E5DED1
D |  |  |  |  |  |  |  |  |  |  |  |  |  |  |  |  |  |  |  |  |  | ads1298 | ADS1298 | U | Reference
D |  |  |  |  |  |  |  |  |  |  |  |  |  |  |  |  |  |  |  |  |  | ads1298 | ADS1298 | ADS1298 | Value
D |  |  |  |  |  |  |  |  |  |  |  |  |  |  |  |  |  |  |  |  |  | ads1298 | ADS1298 |  |  | 1 | IN8N | input
D |  |  |  |  |  |  |  |  |  |  |  |  |  |  |  |  |  |  |  |  |  | ads1298 | ADS1298 |  |  | 2 | IN8P | input
D |  |  |  |  |  |  |  |  |  |  |  |  |  |  |  |  |  |  |  |  |  | ads1298 | ADS1298 |  |  | 3 | IN7N | input
D |  |  |  |  |  |  |  |  |  |  |  |  |  |  |  |  |  |  |  |  |  | ads1298 | ADS1298 |  |  | 4 | IN7P | input
D |  |  |  |  |  |  |  |  |  |  |  |  |  |  |  |  |  |  |  |  |  | ads1298 | ADS1298 |  |  | 5 | IN6N | input
D |  |  |  |  |  |  |  |  |  |  |  |  |  |  |  |  |  |  |  |  |  | ads1298 | ADS1298 |  |  | 6 | IN6P | input
D |  |  |  |  |  |  |  |  |  |  |  |  |  |  |  |  |  |  |  |  |  | ads1298 | ADS1298 |  |  | 7 | IN5N | input
D |  |  |  |  |  |  |  |  |  |  |  |  |  |  |  |  |  |  |  |  |  | ads1298 | ADS1298 |  |  | 8 | IN5P | input
D |  |  |  |  |  |  |  |  |  |  |  |  |  |  |  |  |  |  |  |  |  | ads1298 | ADS1298 |  |  | 9 | IN4N | input
D |  |  |  |  |  |  |  |  |  |  |  |  |  |  |  |  |  |  |  |  |  | ads1298 | ADS1298 |  |  | 10 | IN4P | input
D |  |  |  |  |  |  |  |  |  |  |  |  |  |  |  |  |  |  |  |  |  | ads1298 | ADS1298 |  |  | 11 | IN3N | input
D |  |  |  |  |  |  |  |  |  |  |  |  |  |  |  |  |  |  |  |  |  | ads1298 | ADS1298 |  |  | 12 | IN3P | input
D |  |  |  |  |  |  |  |  |  |  |  |  |  |  |  |  |  |  |  |  |  | ads1298 | ADS1298 |  |  | 13 | IN2N | input
D |  |  |  |  |  |  |  |  |  |  |  |  |  |  |  |  |  |  |  |  |  | ads1298 | ADS1298 |  |  | 14 | IN2P | input
D |  |  |  |  |  |  |  |  |  |  |  |  |  |  |  |  |  |  |  |  |  | ads1298 | ADS1298 |  |  | 15 | IN1N | input
D |  |  |  |  |  |  |  |  |  |  |  |  |  |  |  |  |  |  |  |  |  | ads1298 | ADS1298 |  |  | 16 | IN1P | input
D |  |  |  |  |  |  |  |  |  |  |  |  |  |  |  |  |  |  |  |  |  | ads1298 | ADS1298 |  |  | 17 | TESTP/PACE_OUT | BiDi
D |  |  |  |  |  |  |  |  |  |  |  |  |  |  |  |  |  |  |  |  |  | ads1298 | ADS1298 |  |  | 18 | TESTN/PACE_OUT2 | BiDi
D |  |  |  |  |  |  |  |  |  |  |  |  |  |  |  |  |  |  |  |  |  | ads1298 | ADS1298 |  |  | 19 | AVDD | power_in
D |  |  |  |  |  |  |  |  |  |  |  |  |  |  |  |  |  |  |  |  |  | ads1298 | ADS1298 |  |  | 20 | AVSS | power_in
D |  |  |  |  |  |  |  |  |  |  |  |  |  |  |  |  |  |  |  |  |  | ads1298 | ADS1298 |  |  | 21 | AVDD | power_in
D |  |  |  |  |  |  |  |  |  |  |  |  |  |  |  |  |  |  |  |  |  | ads1298 | ADS1298 |  |  | 22 | AVDD | power_in
D |  |  |  |  |  |  |  |  |  |  |  |  |  |  |  |  |  |  |  |  |  | ads1298 | ADS1298 |  |  | 23 | AVSS | power_in
D |  |  |  |  |  |  |  |  |  |  |  |  |  |  |  |  |  |  |  |  |  | ads1298 | ADS1298 |  |  | 24 | VREFP | input
D |  |  |  |  |  |  |  |  |  |  |  |  |  |  |  |  |  |  |  |  |  | ads1298 | ADS1298 |  |  | 25 | VREFN | input
D |  |  |  |  |  |  |  |  |  |  |  |  |  |  |  |  |  |  |  |  |  | ads1298 | ADS1298 |  |  | 26 | VCAP4 | passive
D |  |  |  |  |  |  |  |  |  |  |  |  |  |  |  |  |  |  |  |  |  | ads1298 | ADS1298 |  |  | 27 | NC | NotConnected
D |  |  |  |  |  |  |  |  |  |  |  |  |  |  |  |  |  |  |  |  |  | ads1298 | ADS1298 |  |  | 28 | VCAP1 | passive
D |  |  |  |  |  |  |  |  |  |  |  |  |  |  |  |  |  |  |  |  |  | ads1298 | ADS1298 |  |  | 29 | NC | NotConnected
D |  |  |  |  |  |  |  |  |  |  |  |  |  |  |  |  |  |  |  |  |  | ads1298 | ADS1298 |  |  | 30 | VCAP2 | passive
D |  |  |  |  |  |  |  |  |  |  |  |  |  |  |  |  |  |  |  |  |  | ads1298 | ADS1298 |  |  | 31 | RESV1 | passive
D |  |  |  |  |  |  |  |  |  |  |  |  |  |  |  |  |  |  |  |  |  | ads1298 | ADS1298 |  |  | 32 | AVSS | power_in
D |  |  |  |  |  |  |  |  |  |  |  |  |  |  |  |  |  |  |  |  |  | ads1298 | ADS1298 |  |  | 33 | DGND | power_in
D |  |  |  |  |  |  |  |  |  |  |  |  |  |  |  |  |  |  |  |  |  | ads1298 | ADS1298 |  |  | 34 | DIN | input
D |  |  |  |  |  |  |  |  |  |  |  |  |  |  |  |  |  |  |  |  |  | ads1298 | ADS1298 |  |  | 35 | ~PWDN | input
D |  |  |  |  |  |  |  |  |  |  |  |  |  |  |  |  |  |  |  |  |  | ads1298 | ADS1298 |  |  | 36 | ~RESET | input
D |  |  |  |  |  |  |  |  |  |  |  |  |  |  |  |  |  |  |  |  |  | ads1298 | ADS1298 |  |  | 37 | CLK | input
D |  |  |  |  |  |  |  |  |  |  |  |  |  |  |  |  |  |  |  |  |  | ads1298 | ADS1298 |  |  | 38 | START | input
D |  |  |  |  |  |  |  |  |  |  |  |  |  |  |  |  |  |  |  |  |  | ads1298 | ADS1298 |  |  | 39 | ~CS | input
D |  |  |  |  |  |  |  |  |  |  |  |  |  |  |  |  |  |  |  |  |  | ads1298 | ADS1298 |  |  | 40 | SCLK | input
D |  |  |  |  |  |  |  |  |  |  |  |  |  |  |  |  |  |  |  |  |  | ads1298 | ADS1298 |  |  | 41 | DAISY_IN | input
D |  |  |  |  |  |  |  |  |  |  |  |  |  |  |  |  |  |  |  |  |  | ads1298 | ADS1298 |  |  | 42 | GPIO1 | BiDi
D |  |  |  |  |  |  |  |  |  |  |  |  |  |  |  |  |  |  |  |  |  | ads1298 | ADS1298 |  |  | 43 | DOUT | output
D |  |  |  |  |  |  |  |  |  |  |  |  |  |  |  |  |  |  |  |  |  | ads1298 | ADS1298 |  |  | 44 | GPIO2 | BiDi
D |  |  |  |  |  |  |  |  |  |  |  |  |  |  |  |  |  |  |  |  |  | ads1298 | ADS1298 |  |  | 45 | GPIO3 | BiDi
D |  |  |  |  |  |  |  |  |  |  |  |  |  |  |  |  |  |  |  |  |  | ads1298 | ADS1298 |  |  | 46 | GPIO4 | BiDi
D |  |  |  |  |  |  |  |  |  |  |  |  |  |  |  |  |  |  |  |  |  | ads1298 | ADS1298 |  |  | 47 | ~DRDY | output
D |  |  |  |  |  |  |  |  |  |  |  |  |  |  |  |  |  |  |  |  |  | ads1298 | ADS1298 |  |  | 48 | DVDD | power_in
D |  |  |  |  |  |  |  |  |  |  |  |  |  |  |  |  |  |  |  |  |  | ads1298 | ADS1298 |  |  | 49 | DGND | power_in
D |  |  |  |  |  |  |  |  |  |  |  |  |  |  |  |  |  |  |  |  |  | ads1298 | ADS1298 |  |  | 50 | DVDD | power_in
D |  |  |  |  |  |  |  |  |  |  |  |  |  |  |  |  |  |  |  |  |  | ads1298 | ADS1298 |  |  | 51 | DGND | power_in
D |  |  |  |  |  |  |  |  |  |  |  |  |  |  |  |  |  |  |  |  |  | ads1298 | ADS1298 |  |  | 52 | CLKSEL | input
D |  |  |  |  |  |  |  |  |  |  |  |  |  |  |  |  |  |  |  |  |  | ads1298 | ADS1298 |  |  | 53 | AVSS1 | power_in
D |  |  |  |  |  |  |  |  |  |  |  |  |  |  |  |  |  |  |  |  |  | ads1298 | ADS1298 |  |  | 54 | AVDD1 | power_in
D |  |  |  |  |  |  |  |  |  |  |  |  |  |  |  |  |  |  |  |  |  | ads1298 | ADS1298 |  |  | 55 | VCAP3 | passive
D |  |  |  |  |  |  |  |  |  |  |  |  |  |  |  |  |  |  |  |  |  | ads1298 | ADS1298 |  |  | 56 | AVDD | power_in
D |  |  |  |  |  |  |  |  |  |  |  |  |  |  |  |  |  |  |  |  |  | ads1298 | ADS1298 |  |  | 57 | AVSS | power_in
D |  |  |  |  |  |  |  |  |  |  |  |  |  |  |  |  |  |  |  |  |  | ads1298 | ADS1298 |  |  | 58 | AVSS | power_in
D |  |  |  |  |  |  |  |  |  |  |  |  |  |  |  |  |  |  |  |  |  | ads1298 | ADS1298 |  |  | 59 | AVDD | power_in
D |  |  |  |  |  |  |  |  |  |  |  |  |  |  |  |  |  |  |  |  |  | ads1298 | ADS1298 |  |  | 60 | RLDREF | input
D |  |  |  |  |  |  |  |  |  |  |  |  |  |  |  |  |  |  |  |  |  | ads1298 | ADS1298 |  |  | 61 | RLDINV | BiDi
D |  |  |  |  |  |  |  |  |  |  |  |  |  |  |  |  |  |  |  |  |  | ads1298 | ADS1298 |  |  | 62 | RLDIN | input
D |  |  |  |  |  |  |  |  |  |  |  |  |  |  |  |  |  |  |  |  |  | ads1298 | ADS1298 |  |  | 63 | RLDOUT | output
D |  |  |  |  |  |  |  |  |  |  |  |  |  |  |  |  |  |  |  |  |  | ads1298 | ADS1298 |  |  | 64 | WCT | output
D |  |  |  |  |  |  |  |  |  |  |  |  |  |  |  |  |  |  |  |  |  | device | C | C | Reference |  |  |  | Unpolarized capacitor
D |  |  |  |  |  |  |  |  |  |  |  |  |  |  |  |  |  |  |  |  |  | device | C | C | Value |  |  |  | Unpolarized capacitor
D |  |  |  |  |  |  |  |  |  |  |  |  |  |  |  |  |  |  |  |  |  | device | C |  |  | 1 | ~ | passive | Unpolarized capacitor
D |  |  |  |  |  |  |  |  |  |  |  |  |  |  |  |  |  |  |  |  |  | device | C |  |  | 2 | ~ | passive | Unpolarized capacitor
D |  |  |  |  |  |  |  |  |  |  |  |  |  |  |  |  |  |  |  |  |  | device | C |  |  |  |  |  | Unpolarized capacitor | C?
D |  |  |  |  |  |  |  |  |  |  |  |  |  |  |  |  |  |  |  |  |  | device | C |  |  |  |  |  | Unpolarized capacitor | C_????_*
D |  |  |  |  |  |  |  |  |  |  |  |  |  |  |  |  |  |  |  |  |  | device | C |  |  |  |  |  | Unpolarized capacitor | C_????
D |  |  |  |  |  |  |  |  |  |  |  |  |  |  |  |  |  |  |  |  |  | device | C |  |  |  |  |  | Unpolarized capacitor | SMD*_c
D |  |  |  |  |  |  |  |  |  |  |  |  |  |  |  |  |  |  |  |  |  | device | C |  |  |  |  |  | Unpolarized capacitor | Capacitor*
D |  |  |  |  |  |  |  |  |  |  |  |  |  |  |  |  |  |  |  |  |  | conn | CONN_01X16 | P | Reference |  |  |  | Connector 01x16
D |  |  |  |  |  |  |  |  |  |  |  |  |  |  |  |  |  |  |  |  |  | conn | CONN_01X16 | CONN_01X16 | Value |  |  |  | Connector 01x16
D |  |  |  |  |  |  |  |  |  |  |  |  |  |  |  |  |  |  |  |  |  | conn | CONN_01X16 |  |  | 1 | P1 | passive | Connector 01x16
D |  |  |  |  |  |  |  |  |  |  |  |  |  |  |  |  |  |  |  |  |  | conn | CONN_01X16 |  |  | 2 | P2 | passive | Connector 01x16
D |  |  |  |  |  |  |  |  |  |  |  |  |  |  |  |  |  |  |  |  |  | conn | CONN_01X16 |  |  | 3 | P3 | passive | Connector 01x16
D |  |  |  |  |  |  |  |  |  |  |  |  |  |  |  |  |  |  |  |  |  | conn | CONN_01X16 |  |  | 4 | P4 | passive | Connector 01x16
D |  |  |  |  |  |  |  |  |  |  |  |  |  |  |  |  |  |  |  |  |  | conn | CONN_01X16 |  |  | 5 | P5 | passive | Connector 01x16
D |  |  |  |  |  |  |  |  |  |  |  |  |  |  |  |  |  |  |  |  |  | conn | CONN_01X16 |  |  | 6 | P6 | passive | Connector 01x16
D |  |  |  |  |  |  |  |  |  |  |  |  |  |  |  |  |  |  |  |  |  | conn | CONN_01X16 |  |  | 7 | P7 | passive | Connector 01x16
D |  |  |  |  |  |  |  |  |  |  |  |  |  |  |  |  |  |  |  |  |  | conn | CONN_01X16 |  |  | 8 | P8 | passive | Connector 01x16
D |  |  |  |  |  |  |  |  |  |  |  |  |  |  |  |  |  |  |  |  |  | conn | CONN_01X16 |  |  | 9 | P9 | passive | Connector 01x16
D |  |  |  |  |  |  |  |  |  |  |  |  |  |  |  |  |  |  |  |  |  | conn | CONN_01X16 |  |  | 10 | P10 | passive | Connector 01x16
D |  |  |  |  |  |  |  |  |  |  |  |  |  |  |  |  |  |  |  |  |  | conn | CONN_01X16 |  |  | 11 | P11 | passive | Connector 01x16
D |  |  |  |  |  |  |  |  |  |  |  |  |  |  |  |  |  |  |  |  |  | conn | CONN_01X16 |  |  | 12 | P12 | passive | Connector 01x16
D |  |  |  |  |  |  |  |  |  |  |  |  |  |  |  |  |  |  |  |  |  | conn | CONN_01X16 |  |  | 13 | P13 | passive | Connector 01x16
D |  |  |  |  |  |  |  |  |  |  |  |  |  |  |  |  |  |  |  |  |  | conn | CONN_01X16 |  |  | 14 | P14 | passive | Connector 01x16
D |  |  |  |  |  |  |  |  |  |  |  |  |  |  |  |  |  |  |  |  |  | conn | CONN_01X16 |  |  | 15 | P15 | passive | Connector 01x16
D |  |  |  |  |  |  |  |  |  |  |  |  |  |  |  |  |  |  |  |  |  | conn | CONN_01X16 |  |  | 16 | P16 | passive | Connector 01x16
D |  |  |  |  |  |  |  |  |  |  |  |  |  |  |  |  |  |  |  |  |  | conn | CONN_01X16 |  |  |  |  |  | Connector 01x16 | Pin_Header_Straight_1X16
D |  |  |  |  |  |  |  |  |  |  |  |  |  |  |  |  |  |  |  |  |  | conn | CONN_01X16 |  |  |  |  |  | Connector 01x16 | Pin_Header_Angled_1X16
D |  |  |  |  |  |  |  |  |  |  |  |  |  |  |  |  |  |  |  |  |  | conn | CONN_01X16 |  |  |  |  |  | Connector 01x16 | Socket_Strip_Straight_1X16
D |  |  |  |  |  |  |  |  |  |  |  |  |  |  |  |  |  |  |  |  |  | conn | CONN_01X16 |  |  |  |  |  | Connector 01x16 | Socket_Strip_Angled_1X16
D |  |  |  |  |  |  |  |  |  |  |  |  |  |  |  |  |  |  |  |  |  | conn | GS2 | GS | Reference
D |  |  |  |  |  |  |  |  |  |  |  |  |  |  |  |  |  |  |  |  |  | conn | GS2 | GS2 | Value
D |  |  |  |  |  |  |  |  |  |  |  |  |  |  |  |  |  |  |  |  |  | conn | GS2 | GS2 | Footprint
D |  |  |  |  |  |  |  |  |  |  |  |  |  |  |  |  |  |  |  |  |  | conn | GS2 |  |  | 1 | G1 | passive
D |  |  |  |  |  |  |  |  |  |  |  |  |  |  |  |  |  |  |  |  |  | conn | GS2 |  |  | 2 | G2 | passive
D |  |  |  |  |  |  |  |  |  |  |  |  |  |  |  |  |  |  |  |  |  | device | INDUCTOR | L | Reference
D |  |  |  |  |  |  |  |  |  |  |  |  |  |  |  |  |  |  |  |  |  | device | INDUCTOR | INDUCTOR | Value
D |  |  |  |  |  |  |  |  |  |  |  |  |  |  |  |  |  |  |  |  |  | device | INDUCTOR |  |  | 1 | 1 | passive
D |  |  |  |  |  |  |  |  |  |  |  |  |  |  |  |  |  |  |  |  |  | device | INDUCTOR |  |  | 2 | 2 | passive
D |  |  |  |  |  |  |  |  |  |  |  |  |  |  |  |  |  |  |  |  |  | device | R | R | Reference |  |  |  | Resistor
D |  |  |  |  |  |  |  |  |  |  |  |  |  |  |  |  |  |  |  |  |  | device | R | R | Value |  |  |  | Resistor
D |  |  |  |  |  |  |  |  |  |  |  |  |  |  |  |  |  |  |  |  |  | device | R |  |  | 1 | ~ | passive | Resistor
D |  |  |  |  |  |  |  |  |  |  |  |  |  |  |  |  |  |  |  |  |  | device | R |  |  | 2 | ~ | passive | Resistor
D |  |  |  |  |  |  |  |  |  |  |  |  |  |  |  |  |  |  |  |  |  | device | R |  |  |  |  |  | Resistor | R_*
D |  |  |  |  |  |  |  |  |  |  |  |  |  |  |  |  |  |  |  |  |  | device | R |  |  |  |  |  | Resistor | Resistor_*
D |  |  |  |  |  |  |  |  |  |  |  |  |  |  |  |  |  |  |  |  |  | holter-cache | SC70_OPAMP | U | Reference
D |  |  |  |  |  |  |  |  |  |  |  |  |  |  |  |  |  |  |  |  |  | holter-cache | SC70_OPAMP | SC70_OPAMP | Value
D |  |  |  |  |  |  |  |  |  |  |  |  |  |  |  |  |  |  |  |  |  | holter-cache | SC70_OPAMP |  |  | 1 | + | input
D |  |  |  |  |  |  |  |  |  |  |  |  |  |  |  |  |  |  |  |  |  | holter-cache | SC70_OPAMP |  |  | 2 | ~ | input
D |  |  |  |  |  |  |  |  |  |  |  |  |  |  |  |  |  |  |  |  |  | holter-cache | SC70_OPAMP |  |  | 3 | - | input
D |  |  |  |  |  |  |  |  |  |  |  |  |  |  |  |  |  |  |  |  |  | holter-cache | SC70_OPAMP |  |  | 4 | ~ | output
D |  |  |  |  |  |  |  |  |  |  |  |  |  |  |  |  |  |  |  |  |  | holter-cache | SC70_OPAMP |  |  | 5 | ~ | input
D |  |  |  |  |  |  |  |  |  |  |  |  |  |  |  |  |  |  |  |  |  | holter-cache | TLV61220 | U | Reference
D |  |  |  |  |  |  |  |  |  |  |  |  |  |  |  |  |  |  |  |  |  | holter-cache | TLV61220 | TLV61220 | Value
D |  |  |  |  |  |  |  |  |  |  |  |  |  |  |  |  |  |  |  |  |  | holter-cache | TLV61220 |  |  | 1 | SW | passive
D |  |  |  |  |  |  |  |  |  |  |  |  |  |  |  |  |  |  |  |  |  | holter-cache | TLV61220 |  |  | 2 | GND | power_in
D |  |  |  |  |  |  |  |  |  |  |  |  |  |  |  |  |  |  |  |  |  | holter-cache | TLV61220 |  |  | 3 | EN | input
D |  |  |  |  |  |  |  |  |  |  |  |  |  |  |  |  |  |  |  |  |  | holter-cache | TLV61220 |  |  | 4 | FB | input
D |  |  |  |  |  |  |  |  |  |  |  |  |  |  |  |  |  |  |  |  |  | holter-cache | TLV61220 |  |  | 5 | VOUT | power_out
D |  |  |  |  |  |  |  |  |  |  |  |  |  |  |  |  |  |  |  |  |  | holter-cache | TLV61220 |  |  | 6 | VBAT | power_in
D |  |  |  |  |  |  |  |  |  |  |  |  |  |  |  |  |  |  |  |  |  | holter-cache | TS5A3159 | U | Reference
D |  |  |  |  |  |  |  |  |  |  |  |  |  |  |  |  |  |  |  |  |  | holter-cache | TS5A3159 | TS5A3159 | Value
D |  |  |  |  |  |  |  |  |  |  |  |  |  |  |  |  |  |  |  |  |  | holter-cache | TS5A3159 |  |  | 1 | ~ | input
D |  |  |  |  |  |  |  |  |  |  |  |  |  |  |  |  |  |  |  |  |  | holter-cache | TS5A3159 |  |  | 2 | GND | power_in
D |  |  |  |  |  |  |  |  |  |  |  |  |  |  |  |  |  |  |  |  |  | holter-cache | TS5A3159 |  |  | 3 | ~ | input
D |  |  |  |  |  |  |  |  |  |  |  |  |  |  |  |  |  |  |  |  |  | holter-cache | TS5A3159 |  |  | 4 | ~ | input
D |  |  |  |  |  |  |  |  |  |  |  |  |  |  |  |  |  |  |  |  |  | holter-cache | TS5A3159 |  |  | 5 | V+ | input
D |  |  |  |  |  |  |  |  |  |  |  |  |  |  |  |  |  |  |  |  |  | holter-cache | TS5A3159 |  |  | 6 | ~ | input
D |  |  |  |  |  |  |  |  |  |  |  |  |  |  |  |  |  |  |  |  |  |  |  |  |  |  |  |  |  |  | device | /usr/share/kicad/library/device.lib
D |  |  |  |  |  |  |  |  |  |  |  |  |  |  |  |  |  |  |  |  |  |  |  |  |  |  |  |  |  |  | conn | /usr/share/kicad/library/conn.lib
D |  |  |  |  |  |  |  |  |  |  |  |  |  |  |  |  |  |  |  |  |  |  |  |  |  |  |  |  |  |  | ads1298 | /media/hamid/Entertainment/STUDY DATA/FYP/Mobile ECG Hardware Final/Hardware/ADS Breakout/ads1298.lib
D |  |  |  |  |  |  |  |  |  |  |  |  |  |  |  |  |  |  |  |  |  |  |  |  |  |  |  |  |  |  | holter-cache | /media/hamid/Entertainment/STUDY DATA/FYP/Mobile ECG Hardware Final/Hardware/ADS Breakout/holter-cache.lib
D |  |  |  |  |  |  |  |  |  |  |  |  |  |  |  |  |  |  |  |  |  |  |  |  |  |  |  |  |  |  |  |  | 1 | GND | U6 | 2
D |  |  |  |  |  |  |  |  |  |  |  |  |  |  |  |  |  |  |  |  |  |  |  |  |  |  |  |  |  |  |  |  | 1 | GND | U5 | 2
D |  |  |  |  |  |  |  |  |  |  |  |  |  |  |  |  |  |  |  |  |  |  |  |  |  |  |  |  |  |  |  |  | 1 | GND | C19 | 1
D |  |  |  |  |  |  |  |  |  |  |  |  |  |  |  |  |  |  |  |  |  |  |  |  |  |  |  |  |  |  |  |  | 1 | GND | U4 | 2
D |  |  |  |  |  |  |  |  |  |  |  |  |  |  |  |  |  |  |  |  |  |  |  |  |  |  |  |  |  |  |  |  | 1 | GND | C4 | 2
D |  |  |  |  |  |  |  |  |  |  |  |  |  |  |  |  |  |  |  |  |  |  |  |  |  |  |  |  |  |  |  |  | 1 | GND | U3 | 2
D |  |  |  |  |  |  |  |  |  |  |  |  |  |  |  |  |  |  |  |  |  |  |  |  |  |  |  |  |  |  |  |  | 1 | GND | C5 | 2
D |  |  |  |  |  |  |  |  |  |  |  |  |  |  |  |  |  |  |  |  |  |  |  |  |  |  |  |  |  |  |  |  | 1 | GND | C2 | 2
D |  |  |  |  |  |  |  |  |  |  |  |  |  |  |  |  |  |  |  |  |  |  |  |  |  |  |  |  |  |  |  |  | 1 | GND | C10 | 2
D |  |  |  |  |  |  |  |  |  |  |  |  |  |  |  |  |  |  |  |  |  |  |  |  |  |  |  |  |  |  |  |  | 1 | GND | C11 | 2
D |  |  |  |  |  |  |  |  |  |  |  |  |  |  |  |  |  |  |  |  |  |  |  |  |  |  |  |  |  |  |  |  | 1 | GND | U1 | 41
D |  |  |  |  |  |  |  |  |  |  |  |  |  |  |  |  |  |  |  |  |  |  |  |  |  |  |  |  |  |  |  |  | 1 | GND | C14 | 2
D |  |  |  |  |  |  |  |  |  |  |  |  |  |  |  |  |  |  |  |  |  |  |  |  |  |  |  |  |  |  |  |  | 1 | GND | R7 | 2
D |  |  |  |  |  |  |  |  |  |  |  |  |  |  |  |  |  |  |  |  |  |  |  |  |  |  |  |  |  |  |  |  | 1 | GND | C15 | 2
D |  |  |  |  |  |  |  |  |  |  |  |  |  |  |  |  |  |  |  |  |  |  |  |  |  |  |  |  |  |  |  |  | 1 | GND | U1 | 53
D |  |  |  |  |  |  |  |  |  |  |  |  |  |  |  |  |  |  |  |  |  |  |  |  |  |  |  |  |  |  |  |  | 1 | GND | U1 | 33
D |  |  |  |  |  |  |  |  |  |  |  |  |  |  |  |  |  |  |  |  |  |  |  |  |  |  |  |  |  |  |  |  | 1 | GND | C16 | 2
D |  |  |  |  |  |  |  |  |  |  |  |  |  |  |  |  |  |  |  |  |  |  |  |  |  |  |  |  |  |  |  |  | 1 | GND | U1 | 32
D |  |  |  |  |  |  |  |  |  |  |  |  |  |  |  |  |  |  |  |  |  |  |  |  |  |  |  |  |  |  |  |  | 1 | GND | U1 | 51
D |  |  |  |  |  |  |  |  |  |  |  |  |  |  |  |  |  |  |  |  |  |  |  |  |  |  |  |  |  |  |  |  | 1 | GND | U1 | 23
D |  |  |  |  |  |  |  |  |  |  |  |  |  |  |  |  |  |  |  |  |  |  |  |  |  |  |  |  |  |  |  |  | 1 | GND | U1 | 20
D |  |  |  |  |  |  |  |  |  |  |  |  |  |  |  |  |  |  |  |  |  |  |  |  |  |  |  |  |  |  |  |  | 1 | GND | C12 | 2
D |  |  |  |  |  |  |  |  |  |  |  |  |  |  |  |  |  |  |  |  |  |  |  |  |  |  |  |  |  |  |  |  | 1 | GND | C13 | 2
D |  |  |  |  |  |  |  |  |  |  |  |  |  |  |  |  |  |  |  |  |  |  |  |  |  |  |  |  |  |  |  |  | 1 | GND | U1 | 57
D |  |  |  |  |  |  |  |  |  |  |  |  |  |  |  |  |  |  |  |  |  |  |  |  |  |  |  |  |  |  |  |  | 1 | GND | U1 | 31
D |  |  |  |  |  |  |  |  |  |  |  |  |  |  |  |  |  |  |  |  |  |  |  |  |  |  |  |  |  |  |  |  | 1 | GND | U2 | 2
D |  |  |  |  |  |  |  |  |  |  |  |  |  |  |  |  |  |  |  |  |  |  |  |  |  |  |  |  |  |  |  |  | 1 | GND | U1 | 58
D |  |  |  |  |  |  |  |  |  |  |  |  |  |  |  |  |  |  |  |  |  |  |  |  |  |  |  |  |  |  |  |  | 1 | GND | U1 | 49
D |  |  |  |  |  |  |  |  |  |  |  |  |  |  |  |  |  |  |  |  |  |  |  |  |  |  |  |  |  |  |  |  | 1 | GND | C1 | 2
D |  |  |  |  |  |  |  |  |  |  |  |  |  |  |  |  |  |  |  |  |  |  |  |  |  |  |  |  |  |  |  |  | 1 | GND | U1 | 25
D |  |  |  |  |  |  |  |  |  |  |  |  |  |  |  |  |  |  |  |  |  |  |  |  |  |  |  |  |  |  |  |  | 1 | GND | C6 | 2
D |  |  |  |  |  |  |  |  |  |  |  |  |  |  |  |  |  |  |  |  |  |  |  |  |  |  |  |  |  |  |  |  | 1 | GND | R2 | 2
D |  |  |  |  |  |  |  |  |  |  |  |  |  |  |  |  |  |  |  |  |  |  |  |  |  |  |  |  |  |  |  |  | 1 | GND | C3 | 2
D |  |  |  |  |  |  |  |  |  |  |  |  |  |  |  |  |  |  |  |  |  |  |  |  |  |  |  |  |  |  |  |  | 1 | GND | C9 | 2
D |  |  |  |  |  |  |  |  |  |  |  |  |  |  |  |  |  |  |  |  |  |  |  |  |  |  |  |  |  |  |  |  | 1 | GND | C8 | 2
D |  |  |  |  |  |  |  |  |  |  |  |  |  |  |  |  |  |  |  |  |  |  |  |  |  |  |  |  |  |  |  |  | 1 | GND | R4 | 2
D |  |  |  |  |  |  |  |  |  |  |  |  |  |  |  |  |  |  |  |  |  |  |  |  |  |  |  |  |  |  |  |  | 1 | GND | C7 | 2
D |  |  |  |  |  |  |  |  |  |  |  |  |  |  |  |  |  |  |  |  |  |  |  |  |  |  |  |  |  |  |  |  | 1 | GND | C22 | 2
D |  |  |  |  |  |  |  |  |  |  |  |  |  |  |  |  |  |  |  |  |  |  |  |  |  |  |  |  |  |  |  |  | 1 | GND | C20 | 2
D |  |  |  |  |  |  |  |  |  |  |  |  |  |  |  |  |  |  |  |  |  |  |  |  |  |  |  |  |  |  |  |  | 1 | GND | R5 | 2
D |  |  |  |  |  |  |  |  |  |  |  |  |  |  |  |  |  |  |  |  |  |  |  |  |  |  |  |  |  |  |  |  | 1 | GND | C25 | 2
D |  |  |  |  |  |  |  |  |  |  |  |  |  |  |  |  |  |  |  |  |  |  |  |  |  |  |  |  |  |  |  |  | 1 | GND | C23 | 2
D |  |  |  |  |  |  |  |  |  |  |  |  |  |  |  |  |  |  |  |  |  |  |  |  |  |  |  |  |  |  |  |  | 1 | GND | C21 | 2
D |  |  |  |  |  |  |  |  |  |  |  |  |  |  |  |  |  |  |  |  |  |  |  |  |  |  |  |  |  |  |  |  | 1 | GND | R6 | 2
D |  |  |  |  |  |  |  |  |  |  |  |  |  |  |  |  |  |  |  |  |  |  |  |  |  |  |  |  |  |  |  |  | 1 | GND | CX1 | 2
D |  |  |  |  |  |  |  |  |  |  |  |  |  |  |  |  |  |  |  |  |  |  |  |  |  |  |  |  |  |  |  |  | 1 | GND | P2 | 2
D |  |  |  |  |  |  |  |  |  |  |  |  |  |  |  |  |  |  |  |  |  |  |  |  |  |  |  |  |  |  |  |  | 1 | GND | P1 | 14
D |  |  |  |  |  |  |  |  |  |  |  |  |  |  |  |  |  |  |  |  |  |  |  |  |  |  |  |  |  |  |  |  | 1 | GND | C18 | 2
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

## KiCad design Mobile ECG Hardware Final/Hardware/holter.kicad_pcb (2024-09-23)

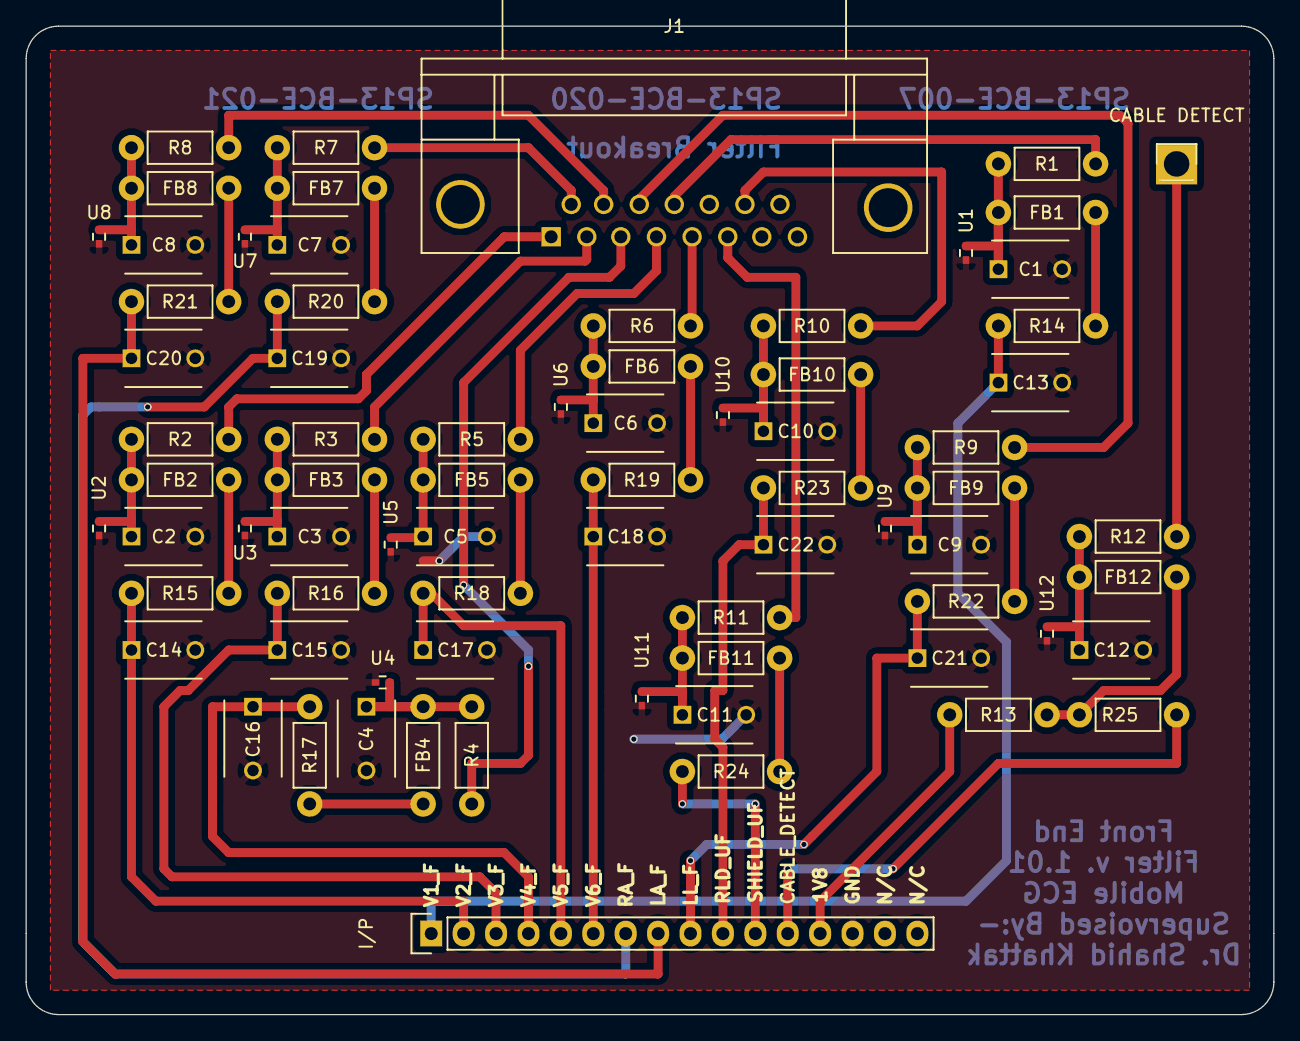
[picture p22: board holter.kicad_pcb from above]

Board: 2 copper layers, 97.8 x 77.5 mm, 74 parts (0 on the bottom side), 50 nets.

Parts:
C1, C2, C3, C4, C5, C6, C7, C8, C9, C10, C11, C12, C13, C14, C15, C16, C17, C18, C19, C20, C21, C22: 47pF; C_Disc_D6_P5
CABLE DETECT: CONN_01X01; Pin_Header_Straight_1x01
FB1, FB2, FB3, FB4, FB5, FB6, FB7, FB8, FB9, FB10, FB11, FB12: FILTER; Resistor_Horizontal_RM7mm
I/P: CONN_01X16; Pin_Header_Straight_1x16
J1: DB15; DB15FC
R1, R2, R3, R4, R5, R6, R7, R8, R9, R10, R11, R12, R24: 470; Resistor_Horizontal_RM7mm
R13: 100k; Resistor_Horizontal_RM7mm
R14, R15, R16, R17, R18, R19, R20, R21, R22, R23: 10k; Resistor_Horizontal_RM7mm
R25: 47k; Resistor_Horizontal_RM7mm
U1, U2, U3, U4, U5, U6, U7, U8, U9, U10, U11, U12: TPD1E10B06DPYR; C_0402

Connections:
+1V8: I/P.13, R13.1
CABLE_DETECT: I/P.12, R25.2
DETECT: CABLE DETECT.1, R12.2
GND: C1.2, C2.2, C3.2, C4.2, C5.2, C6.2, C7.2, C8.2, C9.2, C10.2, C11.2, C12.2, C13.2, C14.2, C15.2, C16.2, C17.2, C18.2, C19.2, C20.2, C21.2, C22.2, I/P.14, U1.2, U2.2, U3.2, U4.2, U5.2, U6.2, U7.2, U8.2, U9.2, U10.2, U11.2, U12.2
LA: J1.10, R8.2
LA_F: C20.1, I/P.8, R21.1
LL: J1.11, R9.2
LL_F: C21.1, I/P.9, R22.1
unnamed: C1.1, FB1.1, R1.1, U1.1
unnamed: C2.1, FB2.1, R2.1, U2.1
unnamed: C3.1, FB3.1, R3.1, U3.1
unnamed: C4.1, FB4.1, R4.1, U4.1
unnamed: C5.1, FB5.1, R5.1, U5.1
unnamed: C6.1, FB6.1, R6.1, U6.1
unnamed: C7.1, FB7.1, R7.1, U7.1
unnamed: C8.1, FB8.1, R8.1, U8.1
unnamed: C9.1, FB9.1, R9.1, U9.1
unnamed: C10.1, FB10.1, R10.1, U10.1
unnamed: C11.1, FB11.1, R11.1, U11.1
unnamed: C12.1, FB12.2, R12.1, U12.1
unnamed: FB1.2, R14.2
unnamed: FB2.2, R15.2
unnamed: FB3.2, R16.2
unnamed: FB4.2, R17.2
unnamed: FB5.2, R18.2
unnamed: FB6.2, R19.2
unnamed: FB7.2, R20.2
unnamed: FB8.2, R21.2
unnamed: FB9.2, R22.2
unnamed: FB10.2, R23.2
unnamed: FB11.2, R24.2
unnamed: FB12.1, R13.2, R25.1
RA: J1.9, R7.2
RA_F: C19.1, I/P.7, R20.1
RLD: J1.14, R10.2
RLD_UF: C22.1, I/P.10, R23.1
SHIELD: J1.6, R11.2
SHIELD_UF: I/P.11, R24.1
V1: J1.12, R1.2
V1_F: C13.1, I/P.1, R14.1
V2: J1.1, R2.2
V2_F: C14.1, I/P.2, R15.1
V3: J1.2, R3.2
V3_F: C15.1, I/P.3, R16.1
V4: J1.3, R4.2
V4_F: C16.1, I/P.4, R17.1
V5: J1.4, R5.2
V5_F: C17.1, I/P.5, R18.1
V6: J1.5, R6.2
V6_F: C18.1, I/P.6, R19.1

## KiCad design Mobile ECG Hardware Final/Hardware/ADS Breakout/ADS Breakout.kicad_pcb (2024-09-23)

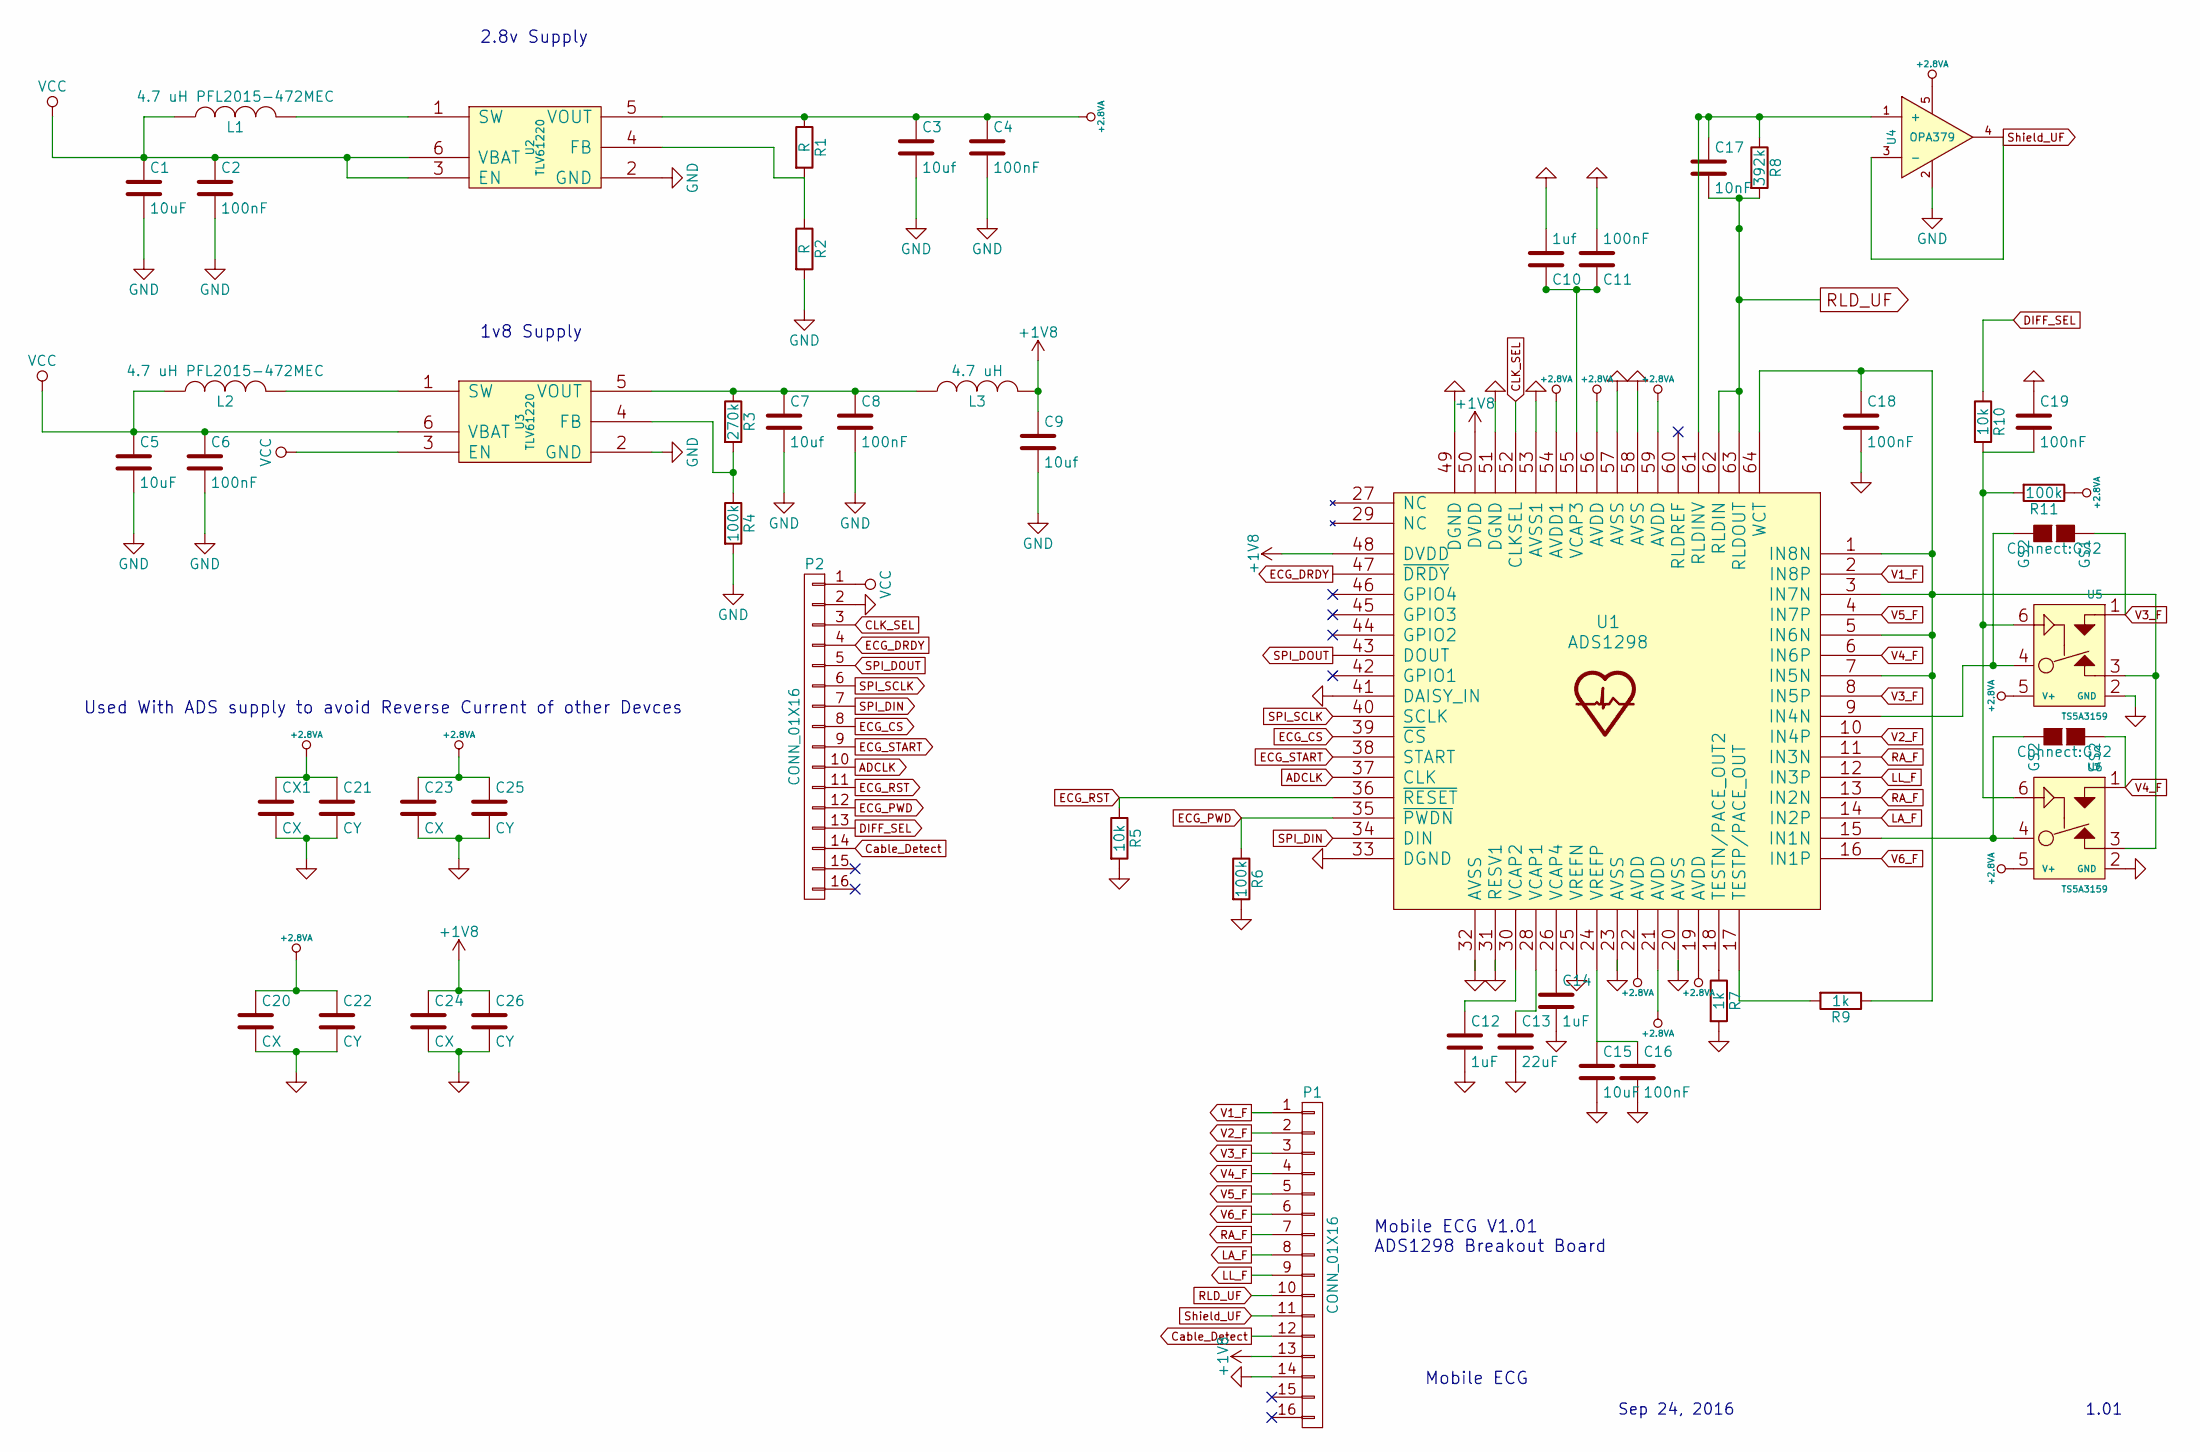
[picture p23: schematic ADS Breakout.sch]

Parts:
C1, C5, C15: 10uF; C_Disc_D3_P2.5
C2, C4, C6, C8, C11, C16, C18, C19: 100nF; C_Disc_D3_P2.5
C3, C7, C9: 10uf; C_Disc_D3_P2.5
C10: 1uf; C_Disc_D3_P2.5
C12, C14: 1uF; C_Disc_D3_P2.5
C13: 22uF; C_Disc_D3_P2.5
C17: 10nF; C_Disc_D3_P2.5
C20, C23, C24: CX; C_Disc_D3_P2.5
C21, C22, C25, C26: CY; C_Disc_D3_P2.5
CX1: CX; C_Disc_D3_P2.5
GS1, GS2: GS2
L1, L2: 4.7 uH PFL2015-472MEC; Resistor_Horizontal_RM7mm
L3: 4.7 uH; Resistor_Horizontal_RM7mm
P1, P2: CONN_01X16; Pin_Header_Straight_1x16
R1, R2: R; Resistor_Horizontal_RM7mm
R3: 270k; Resistor_Horizontal_RM7mm
R4, R6, R11: 100k; Resistor_Horizontal_RM7mm
R5, R10: 10k; Resistor_Horizontal_RM7mm
R7, R9: 1k; Resistor_Horizontal_RM7mm
R8: 392k; Resistor_Horizontal_RM7mm
U1: ADS1298; TQFP-64_10x10mm_Pitch0.5mm
U2, U3: TLV61220; SOT-23-6
U4: OPA379; SC-70-5
U5, U6: TS5A3159; SOT-23-6

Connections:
+1V8: C9.1, C24.1, C26.1, L3.2, P1.13, U1.48 (DVDD), U1.50 (DVDD); also elsewhere on the board
+2.8VA: C3.1, C4.1, C20.1, C21.1, C22.1, C23.1, C25.1, CX1.1, R1.1, R11.1, U1.19 (AVDD), U1.21 (AVDD), U1.22 (AVDD), U1.54 (AVDD1), U1.56 (AVDD), U1.59 (AVDD), U2.5 (VOUT), U4.5, U5.5 (V+), U6.5 (V+)
ADCLK: P2.10, U1.37 (CLK); also elsewhere on the board
CLK_SEL: P2.3, U1.52 (CLKSEL); also elsewhere on the board
DIFF_SEL: P2.13, R10.1; also elsewhere on the board
ECG_CS: P2.8, U1.39 (~CS); also elsewhere on the board
ECG_DRDY: P2.4, U1.47 (~DRDY); also elsewhere on the board
ECG_PWD: P2.12, R6.1, U1.35 (~PWDN); also elsewhere on the board
ECG_RST: P2.11, R5.1, U1.36 (~RESET); also elsewhere on the board
ECG_START: P2.9, U1.38 (START); also elsewhere on the board
GND: C1.2, C2.2, C3.2, C4.2, C5.2, C6.2, C7.2, C8.2, C9.2, C10.2, C11.2, C12.2, C13.2, C14.2, C15.2, C16.2, C18.2, C19.1, C20.2, C21.2, C22.2, C23.2, C24.2, C25.2, C26.2, CX1.2, P1.14, P2.2, R2.2, R4.2, R5.2, R6.2, R7.2, U1.20 (AVSS), U1.23 (AVSS), U1.25 (VREFN), U1.31 (RESV1), U1.32 (AVSS), U1.33 (DGND), U1.41 (DAISY_IN), U1.49 (DGND), U1.51 (DGND), U1.53 (AVSS1), U1.57 (AVSS), U1.58 (AVSS), U2.2 (GND), U3.2 (GND), U4.2, U5.2 (GND), U6.2 (GND); also elsewhere on the board
LA_F: P1.8, U1.14 (IN2P); also elsewhere on the board
LL_F: P1.9, U1.12 (IN3P); also elsewhere on the board
unnamed: C7.1, C8.1, L3.1, R3.1, U3.5 (VOUT)
unnamed: C10.1, C11.1, U1.55 (VCAP3)
unnamed: C12.1, U1.30 (VCAP2)
unnamed: C13.1, U1.28 (VCAP1)
unnamed: C14.1, U1.26 (VCAP4)
unnamed: C15.1, C16.1, U1.24 (VREFP)
unnamed: C17.1, R8.1, U1.61 (RLDINV), U4.1 (+)
unnamed: C18.1, R9.1, U1.1 (IN8N), U1.3 (IN7N), U1.5 (IN6N), U1.7 (IN5N), U1.64 (WCT), U5.3, U6.3
unnamed: C19.2, R10.2, R11.2, U5.6, U6.6
unnamed: GS1.2 (G2), U1.9 (IN4N), U5.4
unnamed: GS2.2 (G2), U1.15 (IN1N), U6.4
unnamed: L1.2, U2.1 (SW)
unnamed: L2.2, U3.1 (SW)
unnamed: P1.12, P2.14
unnamed: R1.2, R2.1, U2.4 (FB)
unnamed: R3.2, R4.1, U3.4 (FB)
unnamed: R7.1, U1.18 (TESTN/PACE_OUT2)
unnamed: R9.2, U1.17 (TESTP/PACE_OUT)
RA_F: P1.7, U1.11 (IN3N), U1.13 (IN2N); also elsewhere on the board
RLD_UF: C17.2, P1.10, R8.2, U1.62 (RLDIN), U1.63 (RLDOUT); also elsewhere on the board
SPI_DIN: P2.7, U1.34 (DIN); also elsewhere on the board
SPI_DOUT: P2.5, U1.43 (DOUT); also elsewhere on the board
SPI_SCLK: P2.6, U1.40 (SCLK); also elsewhere on the board
Shield_UF: P1.11, U4.3 (-), U4.4; also elsewhere on the board
V1_F: P1.1, U1.2 (IN8P); also elsewhere on the board
V2_F: P1.2, U1.10 (IN4P); also elsewhere on the board
V3_F: GS1.1 (G1), P1.3, U1.8 (IN5P), U5.1; also elsewhere on the board
V4_F: GS2.1 (G1), P1.4, U1.6 (IN6P), U6.1; also elsewhere on the board
V5_F: P1.5, U1.4 (IN7P); also elsewhere on the board
V6_F: P1.6, U1.16 (IN1P); also elsewhere on the board
VCC: C1.1, C2.1, C5.1, C6.1, L1.1, L2.1, P2.1, U2.3 (EN), U2.6 (VBAT), U3.3 (EN), U3.6 (VBAT); also elsewhere on the board

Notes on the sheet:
Mobile ECG V1.01 ADS1298 Breakout Board
Mobile ECG
Used With ADS supply to avoid Reverse Current of other Devces
2.8v Supply
1v8 Supply
Sep 24, 2016
1.01

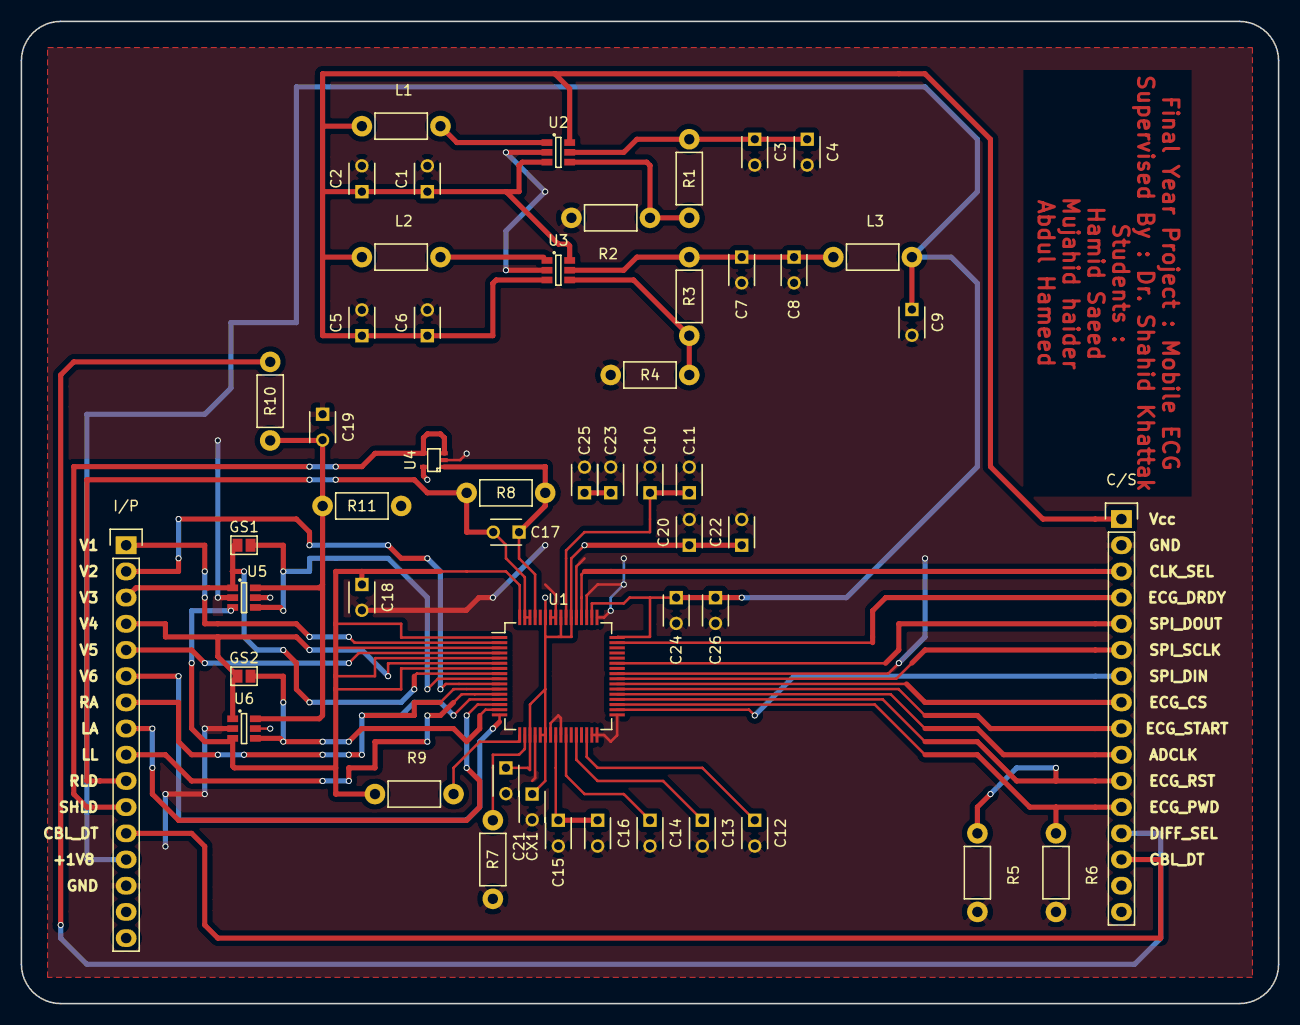
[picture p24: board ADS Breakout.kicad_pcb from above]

Board: 2 copper layers, 121.9 x 95.2 mm, 51 parts (0 on the bottom side), 44 nets.

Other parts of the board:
C/S: CONN_01X16; Pin_Header_Straight_1x16
I/P: CONN_01X16; Pin_Header_Straight_1x16

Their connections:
+1V8: I/P.13; also elsewhere on the board
ADCLK: C/S.10; also elsewhere on the board
CLK_SEL: C/S.3; also elsewhere on the board
Cable_Detect: C/S.14, I/P.12
DIFF_SEL: C/S.13; also elsewhere on the board
ECG_CS: C/S.8; also elsewhere on the board
ECG_DRDY: C/S.4; also elsewhere on the board
ECG_PWD: C/S.12; also elsewhere on the board
ECG_RST: C/S.11; also elsewhere on the board
ECG_START: C/S.9; also elsewhere on the board
GND: C/S.2, I/P.14; also elsewhere on the board
LA_F: I/P.8; also elsewhere on the board
LL_F: I/P.9; also elsewhere on the board
RA_F: I/P.7; also elsewhere on the board
RLD_UF: I/P.10; also elsewhere on the board
SPI_DIN: C/S.7; also elsewhere on the board
SPI_DOUT: C/S.5; also elsewhere on the board
SPI_SCLK: C/S.6; also elsewhere on the board
Shield_UF: I/P.11; also elsewhere on the board
V1_F: I/P.1; also elsewhere on the board
V2_F: I/P.2; also elsewhere on the board
V3_F: I/P.3; also elsewhere on the board
V4_F: I/P.4; also elsewhere on the board
V5_F: I/P.5; also elsewhere on the board
V6_F: I/P.6; also elsewhere on the board
VCC: C/S.1; also elsewhere on the board

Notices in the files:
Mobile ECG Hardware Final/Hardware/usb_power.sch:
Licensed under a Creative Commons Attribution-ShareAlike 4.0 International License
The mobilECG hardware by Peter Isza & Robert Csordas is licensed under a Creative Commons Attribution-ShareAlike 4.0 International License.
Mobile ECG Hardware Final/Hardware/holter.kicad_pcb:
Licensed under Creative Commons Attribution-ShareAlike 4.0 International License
